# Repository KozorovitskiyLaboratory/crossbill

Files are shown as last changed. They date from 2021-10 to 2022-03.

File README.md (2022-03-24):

# crossbill
Crossbill project covers an open access single objective light-sheet microscopy platform. 
This repository covers the software aspect of this project. More details about this project is accessible at the accompanying bioRxiv pre-print at doi: [10.1101/2021.04.30.442190](https://www.biorxiv.org/content/10.1101/2021.04.30.442190v1.full)

An interactive 3D blender file for assembly and parts list is accessible at [10.5281/zenodo.6380689](https://doi.org/10.5281/zenodo.6380689)

# Installation

OS dependence: Windows
(this dependence is due to the DAQ and stage drivers used in the current project)

#### Installation pre-requisite (hardware specific)
Install Instacal (from Measurement Computing) and MCL (MadCityLabs) drivers. This is not required for installation of *crossbill*, but is essential to successfully run the GUI. 

Download this repository, unzip it and get to the /dist folder. 

Run the following on the anaconda (https://www.anaconda.com/products/individual-d) commpand prompt. 

Note: Admin previledges are required on this command prompt to be able to create required environment.

`pip install crossbill-0.0.1-py3-none-any.whl` (this .whl file is in the /dist folder)

Above is the most preferred approach, but alternate ones are listed below:

#### Approach 1. Building *crossbill* environment using setup file / pip:  

  Download crossbill repository, unzip it, get to the folder containing setup.cfg file and then use the following:
  
  ```python
  conda create -n crossbill pip
  conda activate crossbill
  pip install -e . 
  ```

#### Approach 2. Building *crossbill* environment line by line using conda (and pip):

  ```python
  conda create -n crossbill python numpy pyqt qtpy qdarkstyle pip
  conda activate crossbill
  conda install -c conda-forge emoji
  pip install mcculw 
  ```

Once installed, get to the `crossbill-mini` directory (download it from github or zenodo), and run `crossbill-mini.py` file with python:

```python
cd crossbill-mini
python crossbill-mini.py
```
Note: src folder contents may be required to be manually copied to the crossbill-mini folder if 2nd approach for installation was used. 

Some known errors:
- from crossbill.daq import MCCdaq
(If an error shows up related to this line of code, it is likely due to missing Instacal - ensure that Instacal - from Measurement Computing - was installed properly.)

## Folders available in the `crossbill` project

### chamber
This contains 3D printable files related to the water chamber

### crossbill-mini
This contains a python compatible GUI to provide software support for Crossbill microscope.
This is windows compatible. Compatibility to other OS is limited due to incorporated hardware drivers.

### dist
This contains distribution files which may be used with the preferred `pip install` approach. 

### rpi-pico-crossbill
This contains an arduino compatible code which can be uploaded to a Raspberry Pi Pico board to be used with Crossbill microscope.

### src
This folder has various functions/methods associated with DAQ and Stage.

# License:

Caution: This project (software) is in alpha phase of development!
____________________________
MIT License

Copyright (c) 2021 Manish Kumar

Permission is hereby granted, free of charge, to any person obtaining a copy
of this software and associated documentation files (the "Software"), to deal
in the Software without restriction, including without limitation the rights
to use, copy, modify, merge, publish, distribute, sublicense, and/or sell
copies of the Software, and to permit persons to whom the Software is
furnished to do so, subject to the following conditions:

The above copyright notice and this permission notice shall be included in all
copies or substantial portions of the Software.

THE SOFTWARE IS PROVIDED "AS IS", WITHOUT WARRANTY OF ANY KIND, EXPRESS OR
IMPLIED, INCLUDING BUT NOT LIMITED TO THE WARRANTIES OF MERCHANTABILITY,
FITNESS FOR A PARTICULAR PURPOSE AND NONINFRINGEMENT. IN NO EVENT SHALL THE
AUTHORS OR COPYRIGHT HOLDERS BE LIABLE FOR ANY CLAIM, DAMAGES OR OTHER
LIABILITY, WHETHER IN AN ACTION OF CONTRACT, TORT OR OTHERWISE, ARISING FROM,
OUT OF OR IN CONNECTION WITH THE SOFTWARE OR THE USE OR OTHER DEALINGS IN THE
SOFTWARE.
____________________________

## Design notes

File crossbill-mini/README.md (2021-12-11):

# crossbill-mini

Here we have a GUI along with all the required functions/libraries to provide software support for Crossbill.

dependencies folder contains dll files for MadCityLabs stage

icons folder contains icons for the crossbill-mini GUI

Crossbill mini has DAQ and stage control and works in conjunction with any external mode of camera control.

How to get started?

Try the following on the anaconda (https://www.anaconda.com/products/individual-d) commpand prompt.

Note: Admin previledges are required on this command prompt to be able to create required environment. 

Once `crossbill` is installed , get to the directory containing `crossbill-mini.py` file, and run it with python:
```python
cd crossbill-mini
python crossbill-mini.py
```

Congratulations if you could get to the crossbill mini GUI without any errors.

Instacal must be pre-installed before actually using the Measurement Computing DAQ hardware.

Stage will work only if MadCityLabs drivers are properly installed.

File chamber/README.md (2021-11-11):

# chamber

A water chamber is required between MO2 and MO3 in the setup. This chamber is made of flexible sylgard material.
The attached stl file can be used to create the mold for casting sylgard in the chamber shape.

A clip can also be printed out of plastic material to go along the chamber.

*Blender* files are also included for those who want to play with the dimensions to adapt it to their own application.

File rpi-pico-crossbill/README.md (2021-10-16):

## rpi-pico-crossbill.ino
This is an arduino compatible code which can be uploaded to a Raspberry Pi Pico board to be used with Crossbill microscope.

### How to use Arduino IDE to program RPi pico?

1.	Enable RP2040 boards in Tools>Boards>Boards Manager. Look for 'pico' in the search box to get to this board installation.
2.	Connect Pico with ‘bootsel’ pressed
3.	Goto Files>Examples>Basics>Blink and click on upload. This makes the board identifiable by the arduino IDE. 
4.	Check for ports and connect to the correct port where Pico is identified. 
5.	Start programming like a normal arduino board. 

### Pin configurations
- analog input pin: GP26 : machine.ADC(26)
- laser 1 (blue_laser) output pin: GP14 : machine.Pin(14, machine.Pin.OUT)
- laser 2 (green_laser) output pin: GP15 : machine.Pin(15, machine.Pin.OUT)

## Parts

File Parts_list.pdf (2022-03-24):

### Crossbill parts list

Lasers:
473nm 50mW Low Cost Turnkey Laser | Edmund Optics Stock #35-070 | $3,700
532nm 50mW Low Cost Turnkey Laser | Edmund Optics Stock #35-072 | $2,300
Low cost turn key lasers
https://www.edmundoptics.com/f/low-cost-turnkey-lasers/15091/http://www.oemlasersystems.com/
M Series 473nm Laser 50 mW | 473M50, Dragon lasers | $1,160
M Series 532nm Laser 100 mW | 532M100, Dragon lasers | $980
https://www.dragonlasers.com/m-series-532nm-laser-1-300mw.htmlhttps://www.dragonlasers.com/m-series-473nm-laser-50mw.html

Camera:
IMX174, 163 FPS, 76 QE, CMOS | GS3-U3-23S6M-C, Flir | $1,050

Translation stage:
USB Linear slide, 6.4 µm step | Picard Industries | $445
Two axis motorized micropositioning platform with 25mm of travel with 95nm step Size. Third axis manual. | MadCityLabs MMP2 custom modified without encoders | ~$8,000 (RFQ)

http://picardindustries.com/products/linear-motions/usb-linear-slide/

Microscope objectives:
Olympus 60x W - 3 pieces | LUMPLFLN60XW; LWD PLAN FLUOR 60X WTR DIPPING OBJ, NA 1.0, WD 2.0 mm | ~$9,600 (RFQ)
Tube lens - 2 pieces | SWTLU-C, Super wide tube lens FN 26.5 | $800

DAQ:
Analog voltage output
device with 4 high-speed
channels (100 kS/s)
USB-3101FS, MCC | $550

https://www.mccdaq.com/usb-data-acquisition/USB-3100-Series.aspx

Thorlabs Lenses and mirrors:
Scan lens - 2 pieces | CLS-SL | $5,600
Achromatic lenses | AC508-150-A-ML, AC508-100-A-ML | $300
1" Protected Aluminum Elliptical Mirror -2 pcs | PFE10-G01 | $135
Round Protected Aluminum Mirror Ø1" | ME1-G01 | $15 each

Round Protected
Aluminum Mirror Ø1/2"
ME05-G01 | $12 each

Optical scanning systems (Galvanometers):
Large beam galvo (10 mm) | Thorlabs GVS011/M | $1,600
Small beam galvo (<5 mm) | Thorlabs GVS001 | $1,050
Power supply | Traco power TXL 035-1515D | $60

Filter(s) / Dichroic(s):
Dichroic beam combiner | Di01-R405/488/532/635, Semrock | $615
Dichroic beam combiner | FF495-Di03 | $285
Fluorescence filter GFP | MF525-39 | $258
Fluorescence filter TXRED | MF630-69 | $258

Optomechanical components:
Breadboard Handles | BBH1 - 2 pcs | $16
Optical breadboard | MB4560/M - 2 pcs | $800
Ø25.0 mm Pillar Post | RS150/M - 4 pcs | $150
Ø1" Post Holder | RSHT4/M - 4 pcs | $200
Dovetail rails | RLA150/M - 1 pc, RLA300/M - 2 pcs | $210
2 pairs of rail positioners | RCN, RCN1 | $160
Rail carrier | RC1 - 6 pcs | $180
Ø12.7 mm Post Holder | PH20/M - 5 pcs | $35
Ø12.7 mm Optical Post | TR20/M - 5 pcs | $30
Ø12.7 mm Post Holder | PH40/M - 2 pcs | $16
Ø12.7 mm Optical Post | TR40/M - 3 pcs | $18
| TR50/M - 1pc; TR75/M - 3pc;
60 mm Cage Plate | LCP08/M - 6 pcs | $330
30 mm to 60 mm Cage Plate Adapter -5 pcs | LCP02/M | $215
Cage Assembly Rod | ER05-P4 - 2 pcs; ER1-P4 - 1 pc; ER1.5-P4 -1 pc; ER3-P4 - 3 pcs; ER6-P4 - 1 pc; ER12 -8 pcs | $335
Right-Angle Kinematic Elliptical Mirror Mount | KCB1EC/M - 2 pcs | $420

Swivel Base Adapter pack | UPHA-P5 - 3 packs | $335
Right-Angle Clamp for Ø1/2" Posts | RA90/M-P5 | $50
Right-Angle End Clamp for Ø1/2" Posts | RA180/M-P5 | $60
Thread adapters | SM1A3 - 3 pcs; SM2AD41 - 2 pcs; SM1A9 -1 pc; SM1T2 - 1 pc; AP4M3M - 2 pcs; | $160
Table Clamp, L-Shape | CL5A-P5 | $22
Z-Axis Translation Mount | SM1Z | $210
Sliding Filter Mount with Two CFS1-F1 Inserts | CFS1/M | $170
30 mm Cage Cube with Dichroic Filter Mount | CM1-DCH/M - 2 pcs | $350
Lens Mount with Retaining Ring for Ø2" Optics, | LMR2/M | $30
45° Mirror Mount for Ø1/2" Optics | H45A - 2 pcs | $70
Mini-Series Kinematic Mirror Mount for Ø1/2" Optics | MK05/M - 2 pcs | $175
6.5 mm Travel Single-Axis Translation Stage | MS1S/M - 2 pcs | $465
Right-Angle Kinematic Mount for Ø1" Optics, 30 mm Cage Compatible | C45P - 1 pc | $169

3D printed/moulded parts:
Objective chamber | Custom (download stl from github) | --
Chamber clip | Custom (download stl from github) | --

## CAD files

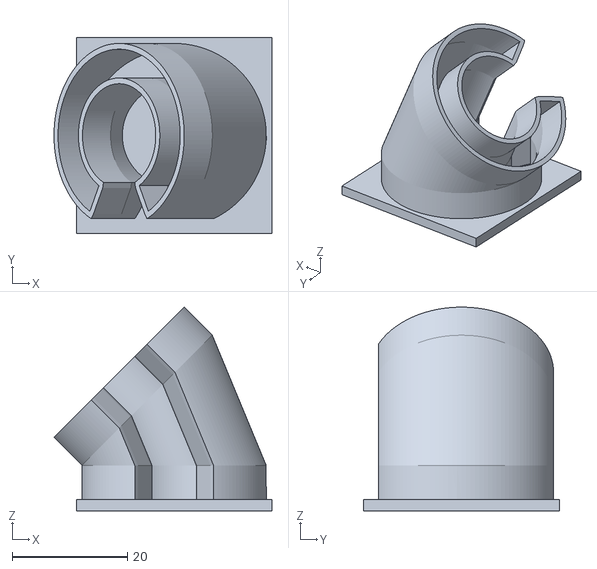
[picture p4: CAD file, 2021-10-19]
chamber/UMO_chamber-Mold_20_30_withbase.stl
37.9 x 34.0 x 35.4

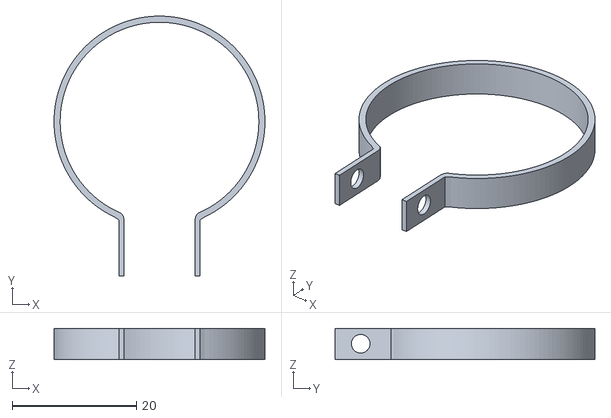
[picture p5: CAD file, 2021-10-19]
chamber/UMO_clip-ID32clip.stl
34.0 x 41.9 x 5.00

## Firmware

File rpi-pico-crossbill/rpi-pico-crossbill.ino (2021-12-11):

/* MIT License

Copyright (c) 2021 Manish Kumar

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
THE SOFTWARE IS PROVIDED "AS IS", WITHOUT WARRANTY OF ANY KIND, EXPRESS OR
IMPLIED, INCLUDING BUT NOT LIMITED TO THE WARRANTIES OF MERCHANTABILITY,
FITNESS FOR A PARTICULAR PURPOSE AND NONINFRINGEMENT. IN NO EVENT SHALL THE
AUTHORS OR COPYRIGHT HOLDERS BE LIABLE FOR ANY CLAIM, DAMAGES OR OTHER
LIABILITY, WHETHER IN AN ACTION OF CONTRACT, TORT OR OTHERWISE, ARISING FROM,
OUT OF OR IN CONNECTION WITH THE SOFTWARE OR THE USE OR OTHER DEALINGS IN THE
SOFTWARE.
*/

// This file is written as a part of the Crossbill project and provides necessary software support for hardware integration.
// Crossbill is detailed at doi: https://doi.org/10.1101/2021.04.30.442190


//## Analog IN - Digital OUT to control two lasers output using one analog input
//# Pin configurations
//# analog input pin: GP26 : machine.ADC(26)
//# laser 1 (blue_laser) output pin: GP14 : machine.Pin(14, machine.Pin.OUT)
//# laser 2 (green_laser) output pin: GP15 : machine.Pin(15, machine.Pin.OUT)

int led_onboard = 25;
int analog_pin = 26;
int blue_laser = 14;
int green_laser = 15;
int val = 0; // hold voltage value 

void setup() {
  // put your setup code here, to run once:
  pinMode(led_onboard, OUTPUT);
  pinMode(analog_pin, INPUT);
  pinMode(blue_laser, OUTPUT);
  pinMode(green_laser, OUTPUT);
  //Serial.begin(115200);           //  setup serial
}

void loop() {
  // put your main code here, to run repeatedly:
  val = analogRead(analog_pin);  // read the input pin. 0-1023 belong to 0-3v3
  //Serial.println(val);          // debug value
  if (val < 300) {
    digitalWrite(led_onboard, LOW);
    digitalWrite(blue_laser, LOW);
    digitalWrite(green_laser, LOW);
  }
  else if (val < 600) {
    digitalWrite(led_onboard, HIGH);
    digitalWrite(blue_laser, HIGH);
    digitalWrite(green_laser, LOW);
  }
  else {
    digitalWrite(led_onboard, HIGH);
    digitalWrite(blue_laser, LOW);
    digitalWrite(green_laser, HIGH);
  }
}
